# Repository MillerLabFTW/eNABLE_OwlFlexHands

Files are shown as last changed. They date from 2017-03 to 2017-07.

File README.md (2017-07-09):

# eNABLE_OwlFlexHands
**OwlFlex Left and Right Hand Files**  
**Miller Lab Physiologic Systems Engineering and Advanced Materials**  
[Miller Lab](millerlab.rice.edu)  
GitHub Logo

**Documentation**
This repository contains scaled Left OwlFlex and Right OwlFlex Hands from 0.6 to 1.0 scale. Please download the files and measure the relevant dimensions using NetFabb or other softwares. 

**Acknowledgements**
This design was modified from the FlexyHand, which was designed by Gyrobot: http://www.thingiverse.com/thing:380665.

Contributors: Akhil Surapaneni, Chris Vangundy, Justin Tang, Angelo Molina-Rossi, Dr. Gloria Gogola, Jordan Miller

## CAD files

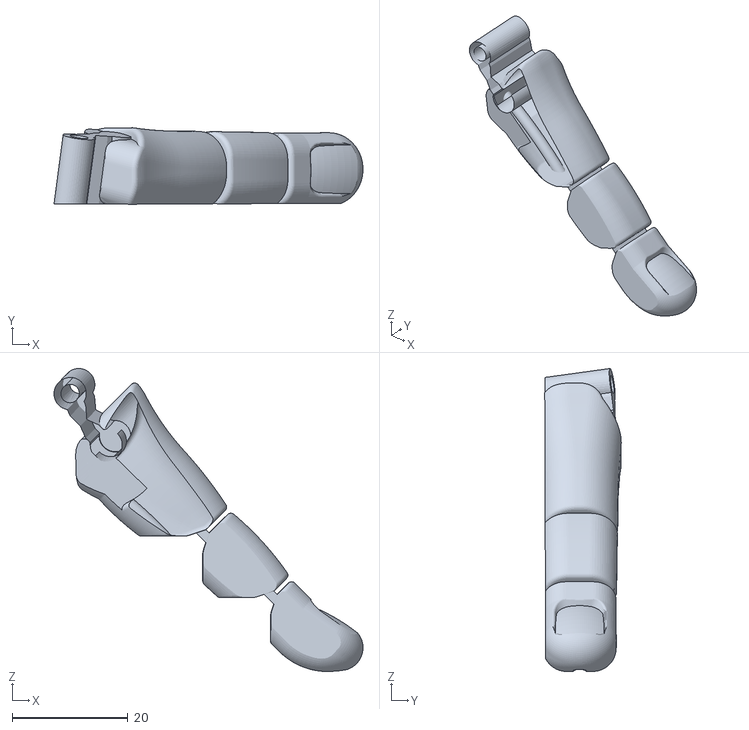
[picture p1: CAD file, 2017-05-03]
0.79 Scale Regular Hinge Fingers/0.79_Regular Hinge Pinky.stl
53.3 x 13.2 x 52.3

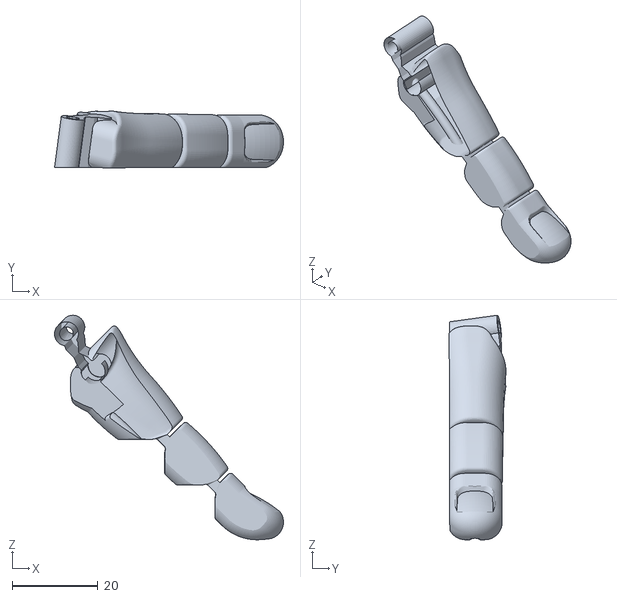
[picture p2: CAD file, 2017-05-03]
0.79 scale Thick Hinge Fingers/0.79_thickhingejointspinky.stl
53.3 x 13.2 x 52.3

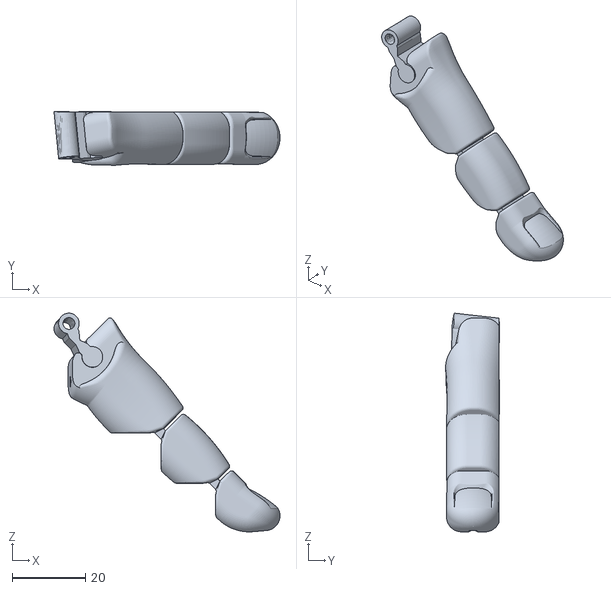
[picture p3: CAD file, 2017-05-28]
0.81 scale Thick Hinge Fingers/0.81_thickhingejointsindex.stl
61.7 x 14.7 x 59.7

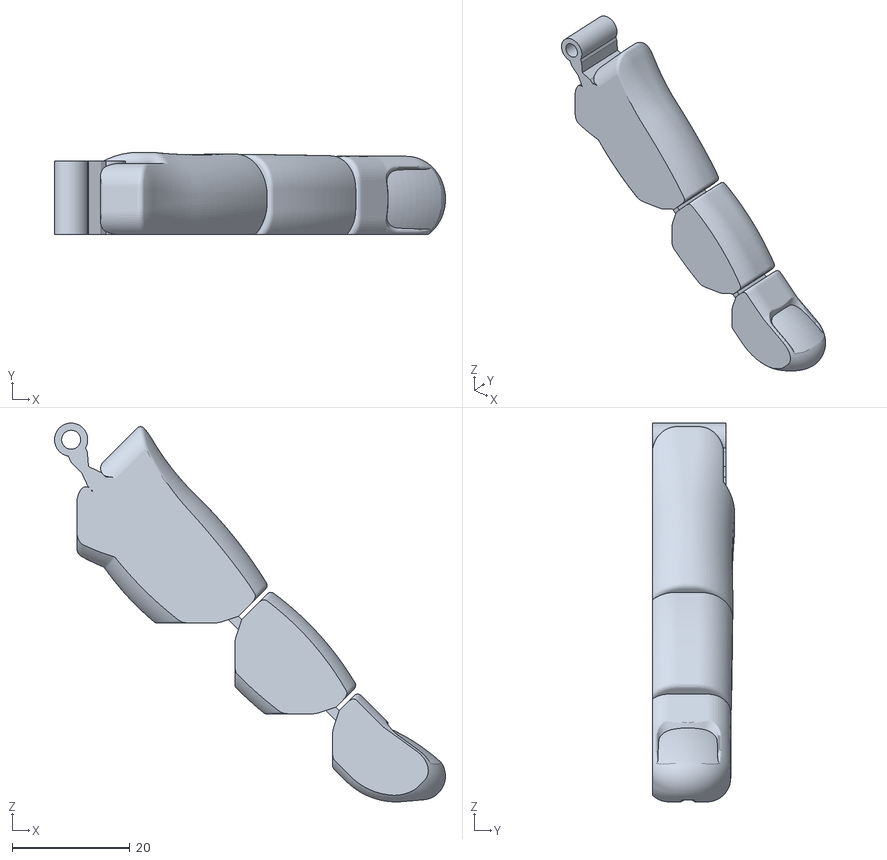
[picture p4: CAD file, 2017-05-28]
0.81 scale_regular hinge fingers/0.81_Regular Hinge Middle Finger .stl
66.5 x 13.9 x 64.4

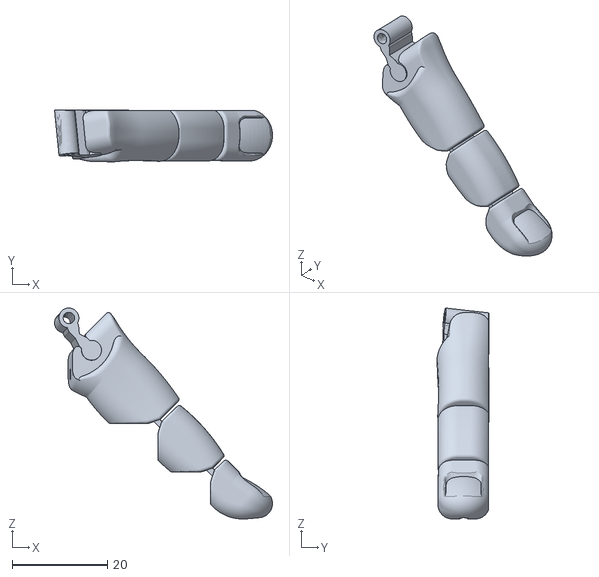
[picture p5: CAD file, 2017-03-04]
Left Hand Owl Flex Palm (0.77-0.84 scale)/0.6 OwlFlex/Flat Index Finger_0.6 .stl
45.7 x 10.9 x 44.2

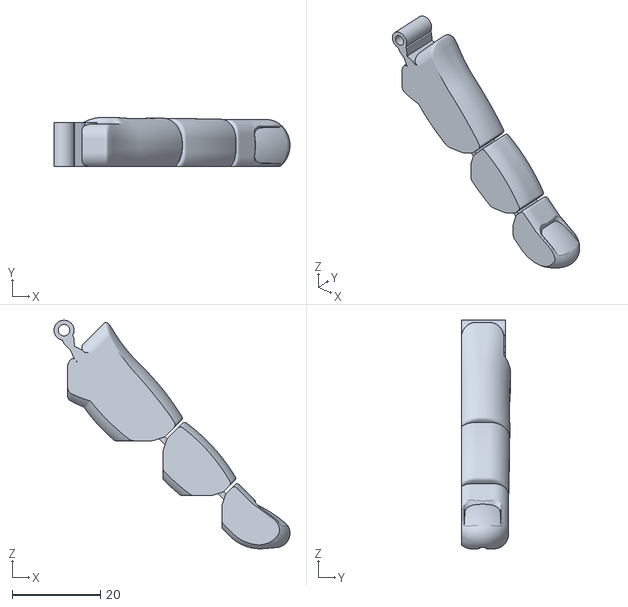
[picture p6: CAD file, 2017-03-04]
Left Hand Owl Flex Palm (0.77-0.84 scale)/0.65 OwlFlex/Flat Middle Finger _0.65.stl
53.4 x 11.2 x 51.7

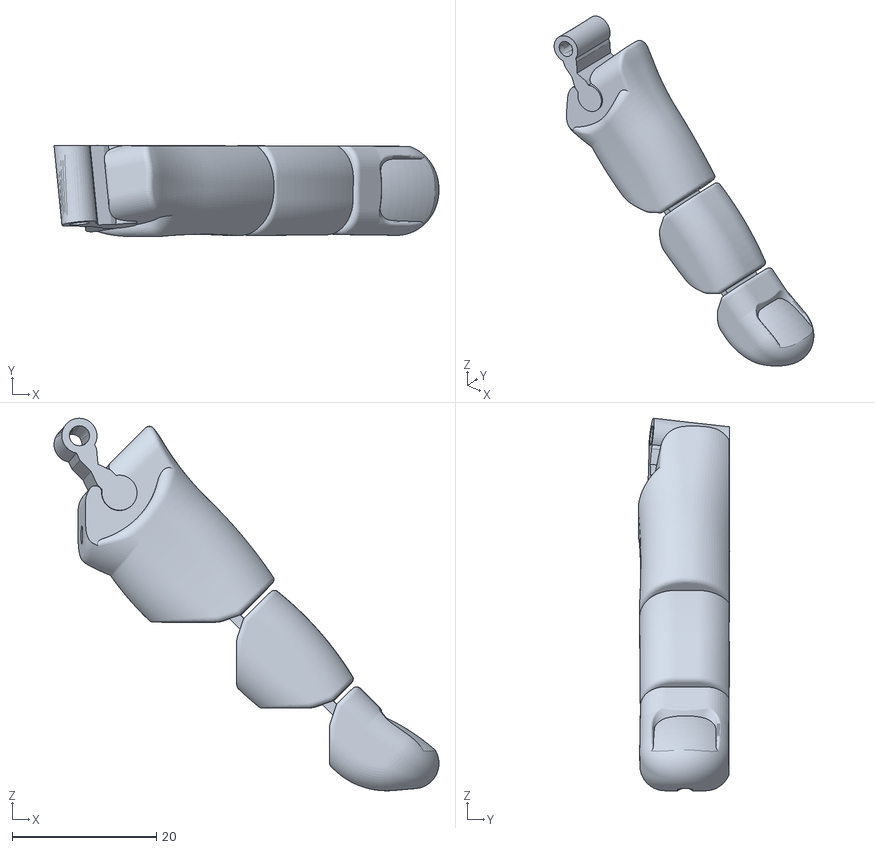
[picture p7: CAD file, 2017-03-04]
Left Hand Owl Flex Palm (0.77-0.84 scale)/0.7 OwlFlex/Flat Index Finger_0.7 .stl
53.3 x 12.7 x 51.6

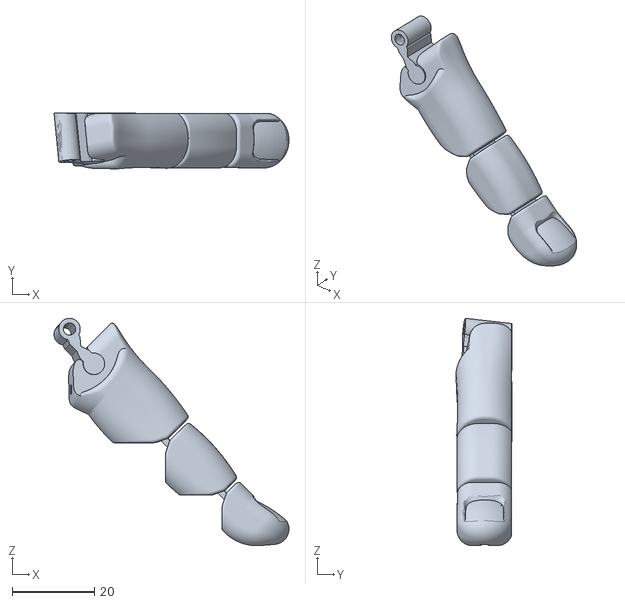
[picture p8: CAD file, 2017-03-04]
Left Hand Owl Flex Palm (0.77-0.84 scale)/0.75 OwlFlex/Flat Index Finger_0.75.stl
57.1 x 13.6 x 55.3

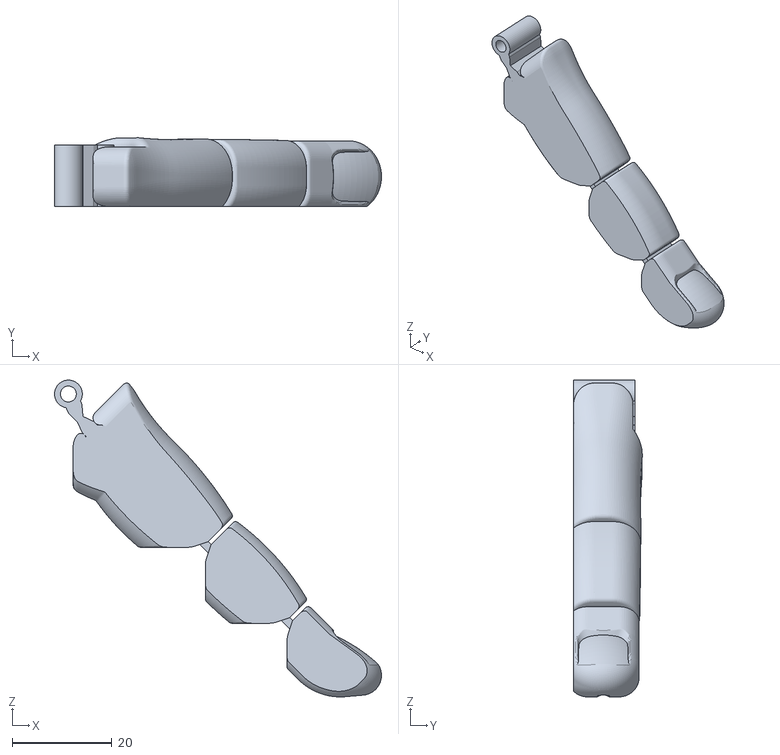
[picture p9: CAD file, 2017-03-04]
Left Hand Owl Flex Palm (0.77-0.84 scale)/0.8 Owl Flex/Flat Middle Finger_0.8.stl
65.7 x 13.8 x 63.6

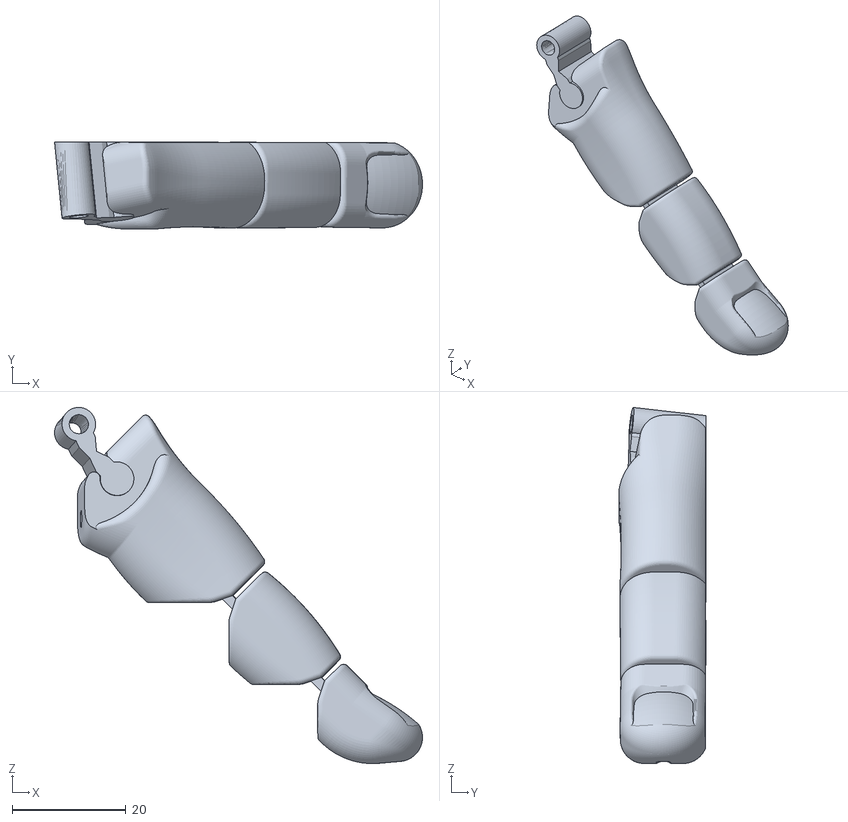
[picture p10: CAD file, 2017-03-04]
Left Hand Owl Flex Palm (0.77-0.84 scale)/0.85 OwlFlex/Flat Index Finger_0.85.stl
64.7 x 15.4 x 62.6

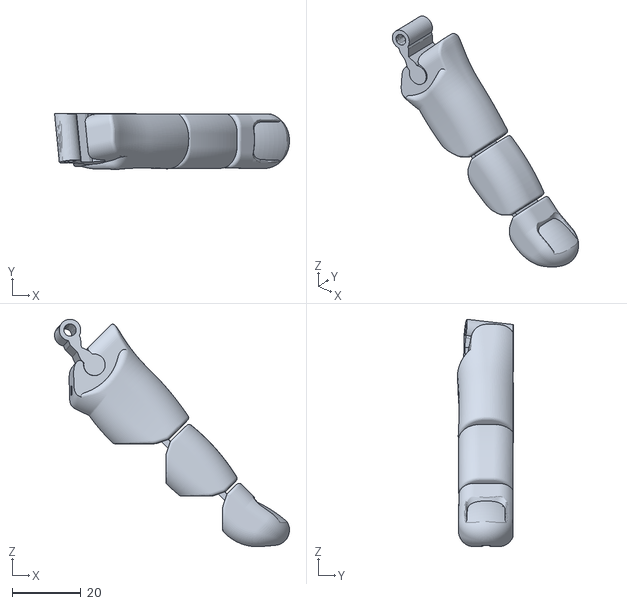
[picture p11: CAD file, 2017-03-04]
Left Hand Owl Flex Palm (0.77-0.84 scale)/0.90 OwlFlex/Flat Index Finger_0.9.stl
68.5 x 16.3 x 66.3

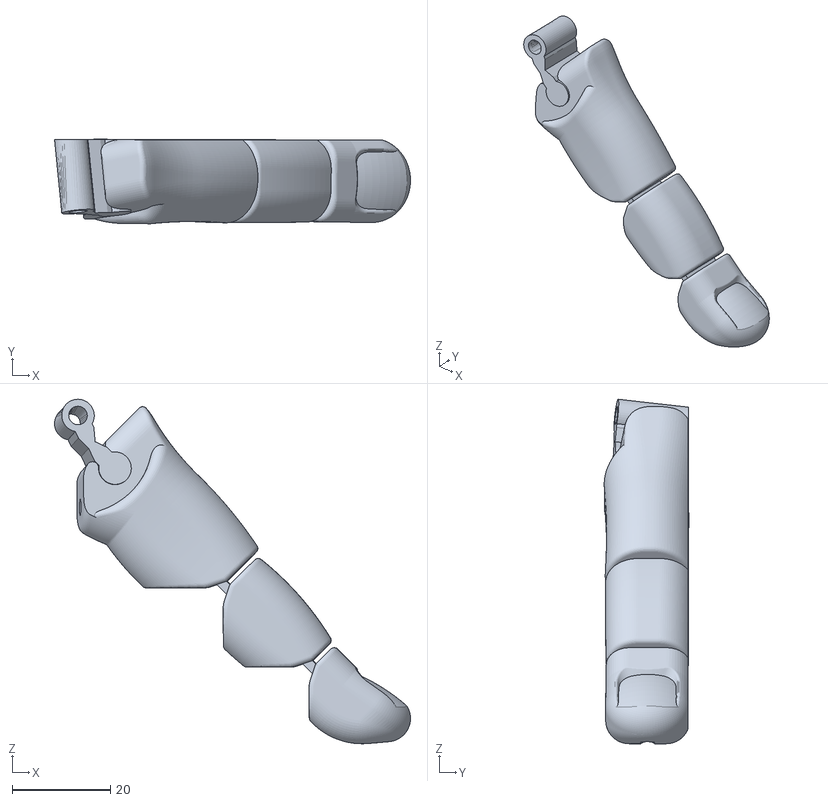
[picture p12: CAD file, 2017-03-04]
Left Hand Owl Flex Palm (0.77-0.84 scale)/0.95 OwlFlex/Flat Index Finger_0.95.stl
72.3 x 17.2 x 70.0

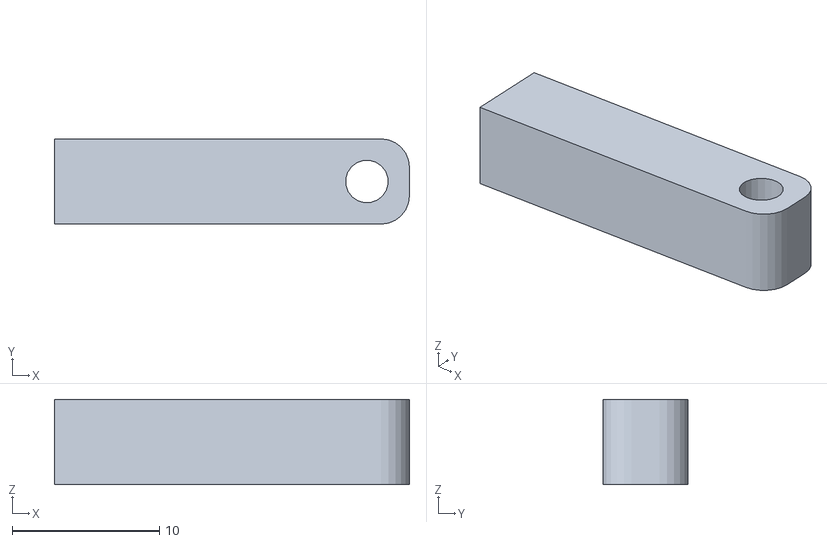
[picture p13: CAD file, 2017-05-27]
Owl Flex Final Design 1.0 Scale/Tensioner-correct-scale.stl
24.1 x 5.78 x 5.78

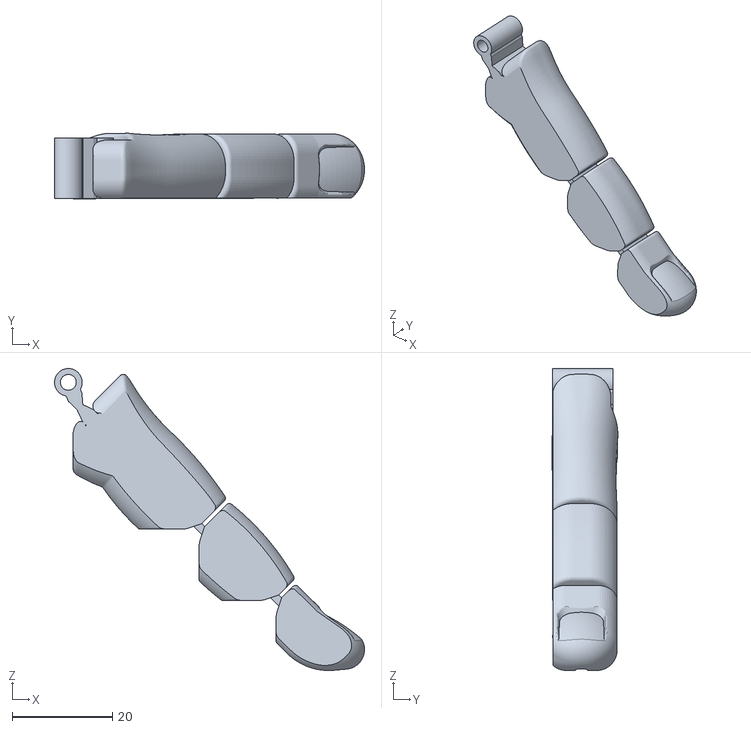
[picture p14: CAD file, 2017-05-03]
0.79 Scale Regular Hinge Fingers/0.79_Regular Hinge Ring Finger.stl
61.8 x 13.1 x 60.2

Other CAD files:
0.79 scale Thick Hinge Fingers/0.79_thickhingejointsthumb.stl
0.81 scale Thick Hinge Fingers/0.81_thickhingejointsthumb.stl
0.81 scale_regular hinge fingers/0.81_Regular Hinge Ring Finger.stl
Left Hand Owl Flex Palm (0.77-0.84 scale)/0.6 OwlFlex/Flat Middle Finger_0.6.stl
0.79 Scale Regular Hinge Fingers/0.79_Regular Hinge Index Finger .stl
0.79 Scale Regular Hinge Fingers/0.79_Regular Hinge Middle Finger .stl
0.79 Scale Regular Hinge Fingers/0.79_Regular Hinge Thumb.stl
0.79 scale Thick Hinge Fingers/0.79_thickhingejointsindex.stl
0.79 scale Thick Hinge Fingers/0.79_thickhingejointsmiddleflat.stl
0.79 scale Thick Hinge Fingers/0.79_thickhingejointsring.stl
0.81 scale Thick Hinge Fingers/0.81_thickhingejointsmiddleflat.stl
0.81 scale Thick Hinge Fingers/0.81_thickhingejointspinky.stl
0.81 scale Thick Hinge Fingers/0.81_thickhingejointsring.stl
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

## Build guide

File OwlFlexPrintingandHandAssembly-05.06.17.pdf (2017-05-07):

OwlFlex Hand Printing and Assembly By Akhil Surapaneni, Chris Vangundy Printing Overview

Part | Filename | Material | Infill | Printer | Extruder Temp | Bed Temp | Print Speed
Gauntlet | Gauntlet-Long-cor rect-scale.stl | PLA | 80% | Ultimaker 2 | 210C | 60 | 50 mm/sec
Fingers (Typical Hand Set) | Regular Hinge Index Finger .stl, Regular Hinge Middle Finger .stl, Regular Hinge Pinky.stl, Regular Hinge Ring Finger.stl, Regular Hinge Thumb.stl | Semiflex | 35% | M2 or Prusa | 235C on M2/ 230C on Prusa | 50C on Prusa/ 40C on M2 | 16.67 on M2 / 30% speed manual override on Prusa
Fingers (Alternate Hand Set) | thickhingejointsind ex.stl, thickhingejointsmi ddleflat.stl, thickhingejointspin ky.stl, thickhingejointsrin g.stl , thickhingejointsth umb.stl | Ninjaflex | 35% | M2 or Prusa | 235C on M2/ 230C on Prusa | 50C on Prusa/ 40C on M2 | 16.67 on M2 / 30% speed manual override on Prusa
Palm | OwlFlexRightHan d.stl or OwlFlexPalm.stl (left hand) | Ninjaflex | 35% | M2 or Prusa | 235C on M2/ 230C on Prusa | 50C on Prusa/ 40C on M2 | 16.67 on M2 / 50% speed manual override on Prusa
Hinges | FFX_-_Flexy-Hing e_Wrist.stl | Ninjaflex | 35% | M2 or Prusa | 235C on M2/ 230C on Prusa | 50C on Prusa/ 40C on M2 | 16.67 on M2 / 50% speed manual override on Prusa

Pins | Tensioner-correct-
scale.stl
PLA | 80% | Ultimaker 2 | 210C | 60 | 50 mm/sec

Parts:
Please download the following files from MillerLabFTW/eNABLE_OwlFlexHands/Owl Flex Final Design 1.0 Scale on Github

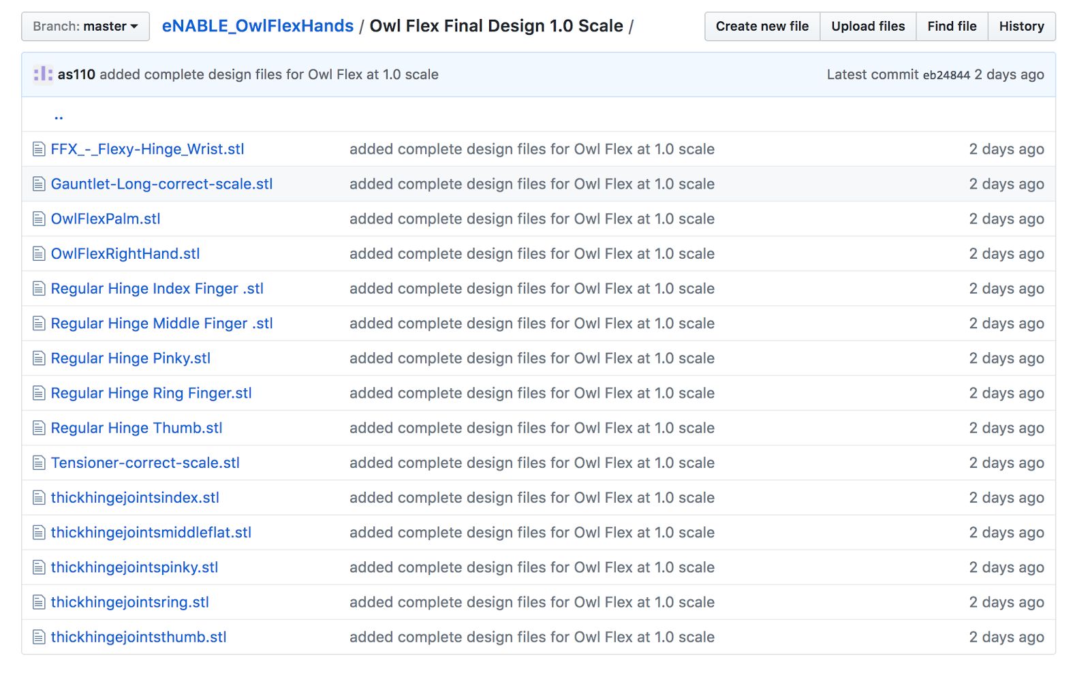
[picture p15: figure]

Fig.1: Github Folder with Design Files
- Palm: OwlFlexRightHand.stl or OwlFlexPalm.stl (left hand)
- Gauntlet: Gauntlet-Long-correct-scale.stl
- Fingers (please download either the Regular Hinge or Thick Hinge Fingers)
- Regular Hinge Fingers:Regular Hinge Index Finger .stl, Regular Hinge Middle Finger .stl, Regular Hinge Pinky.stl, Regular Hinge Ring Finger.stl, Regular Hinge Thumb.stl
- thickhingejointsindex.stl, thickhingejointsmiddleflat.stl, thickhingejointspinky.stl, thickhingejointsring.stl, thickhingejointsthumb.stl
- Wrist Hinges: FFX_-_Flexy-Hinge_Wrist.stl
- Tensioner Pin: Tensioner-correct-scale.stl
Scaling
Please scale the palm so that the patient’s orthoplast socket is a snug fit inside of it. At 1.0 scale, the palm is 65mm across the wrist as seen in Fig.2 below.Please use one of the shoebox palms for reference.

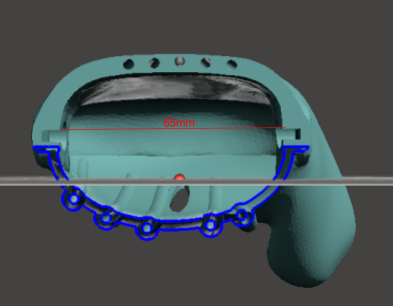
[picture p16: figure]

Fig.2: Width of Palm across Wrist Please download the correct sized palm from the eNABLE_OwlFlexHands repository. For the other parts, please scale them to the same scale as the palm.
IN THE FUTURE: We want to be able to match the fingers scale so that they are the same size as the patient’s biological fingers. Please update the protocol once we figure out how to do this.
Slicing
- Palm: Orient the hand as seen in the picture below (Fig.3) and please don’t add any support. It is printed with 35% infill with Ninjaflex.

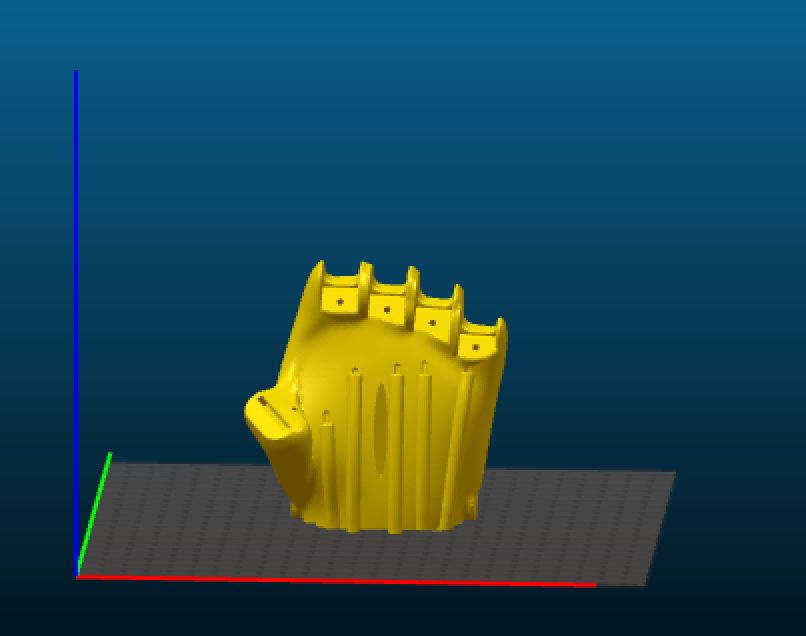
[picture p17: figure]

Fig.3 Palm Printing

When printing on M2, use the M2 profile.
When printing on Prusa, please consult the “Printing Ninjaflex on Prusa i3.docx” file found on the server at People→ eNABLE→ Logistics and Overview. Use the 0.2mm Normal profile and change the infill to 35% (Fig. 4)

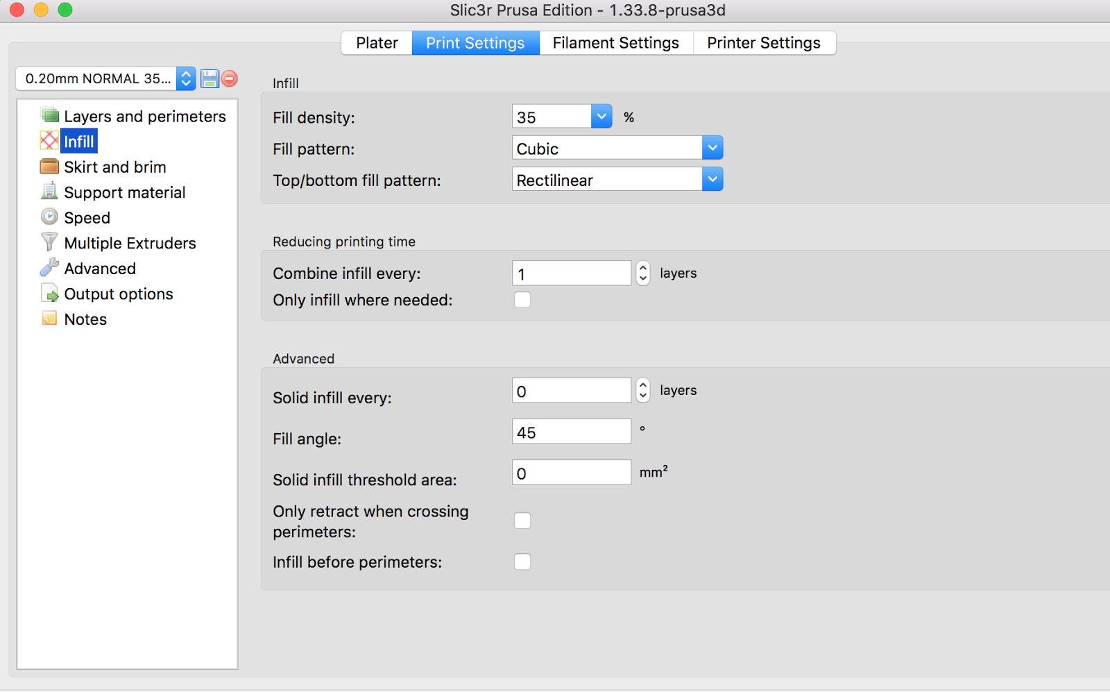
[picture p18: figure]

Fig. 4: Palm Infill Density on Prusa
- Fingers: printed with 35% infill
- When printing Regular Hinge fingers, please insert Semiflex Filament into both the M2 and Prusa printers. Please use the Semiflex profile on the M2 and the 0.2mm Normal 35% Infill profile on the Prusa that we have created for the palm.
- When printing Thick Hinge fingers, please insert Ninjaflex Filament into both the M2 and Prusa printers. Please the M2 profile on the M2 and 0.2mm Normal 35% Infill profile on the Prusa
- When printing fingers on the Prusa, make sure that the manual override speed is set to 30% and the Live Z offset is set to -0.675mm. For more info on where to find those settings, please consult the “Printing Ninjaflex on Prusa” protocol Please orient the fingers so that the flat side is touching the print surface as seen below (Fig.5) and (Fig.6)

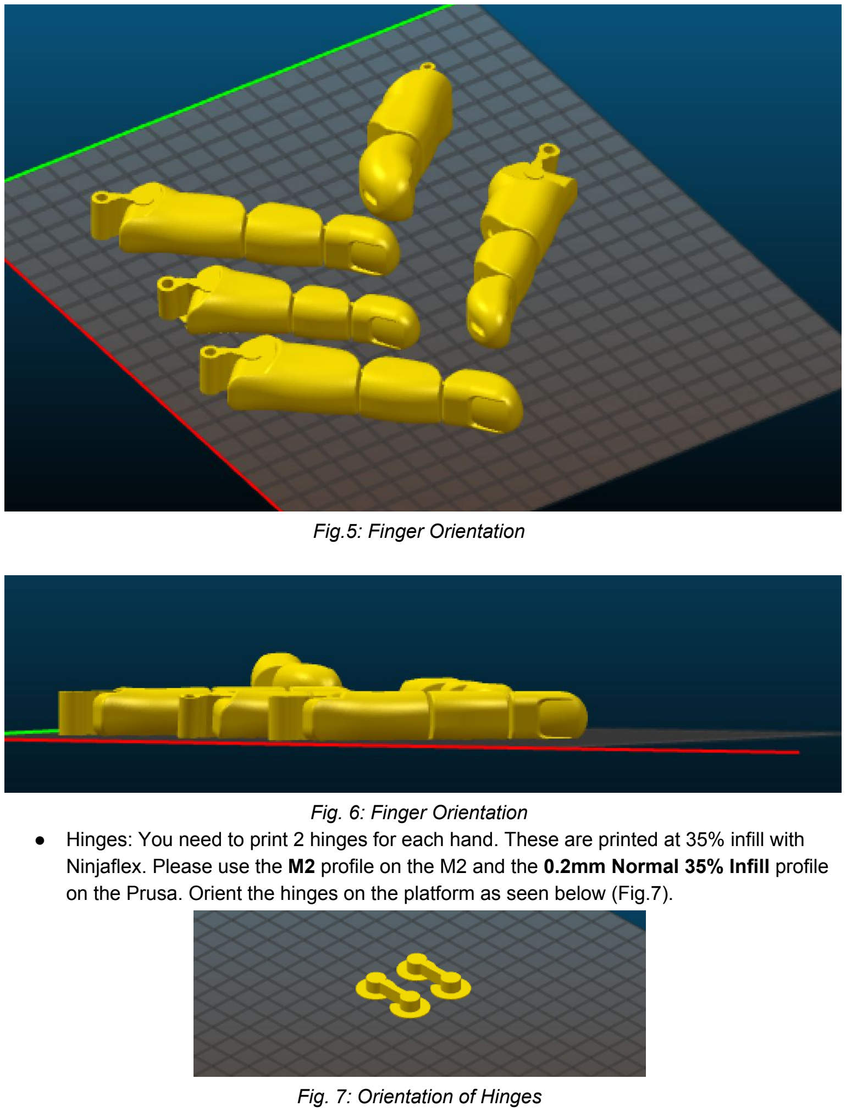
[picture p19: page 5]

Fig.5: Finger Orientation

Fig. 6: Finger Orientation
- Hinges: You need to print 2 hinges for each hand. These are printed at 35% infill with Ninjaflex. Please use the M2 profile on the M2 and the 0.2mm Normal 35% Infill profile on the Prusa. Orient the hinges on the platform as seen below (Fig.7).

Fig. 7: Orientation of Hinges

- Gauntlet: Please print the Gauntlet at 80% infill and use a Brim when printing it. The gauntlet is printed on Ultimaker with PLA filament, so please use Cura to slice the file. The key print settings can be seen in the figure below (Fig.8).

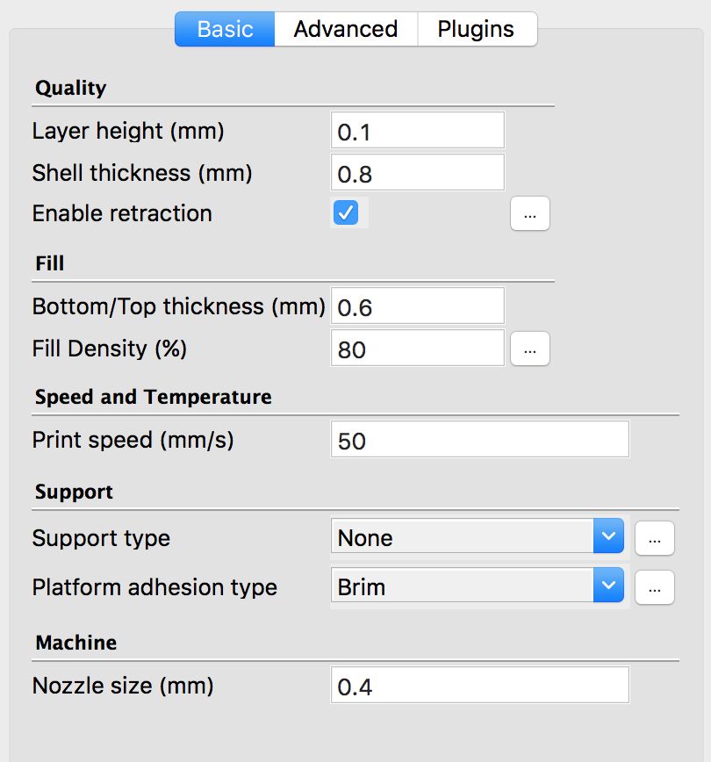
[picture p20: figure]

Fig.8: Gauntlet Printing Profile The orientation of the gauntlet on the platform can be seen in the figure below (Fig.9).

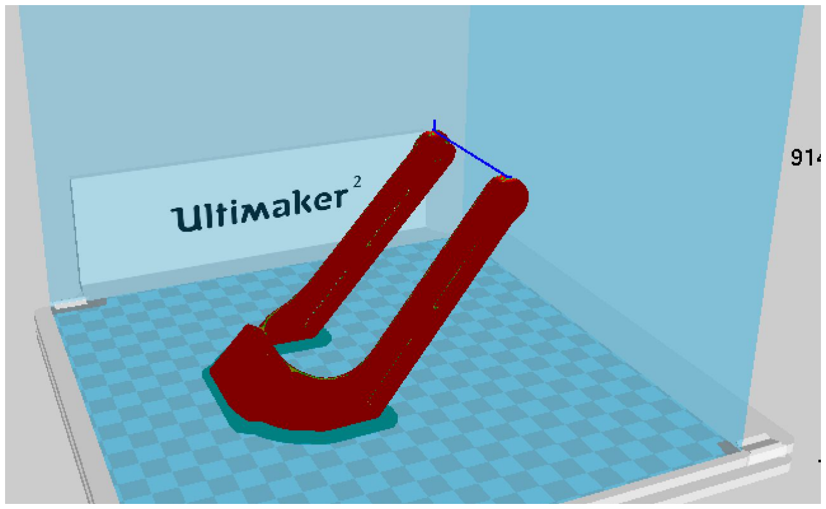
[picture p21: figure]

Fig.9: Gauntlet Printing Orientation
- Pins: You need 5 pins per hand. These are printed with the Ultimaker using PLA. Please use the same profile as you used for the Gauntlet. Orient the pins as seen below (Fig.10).

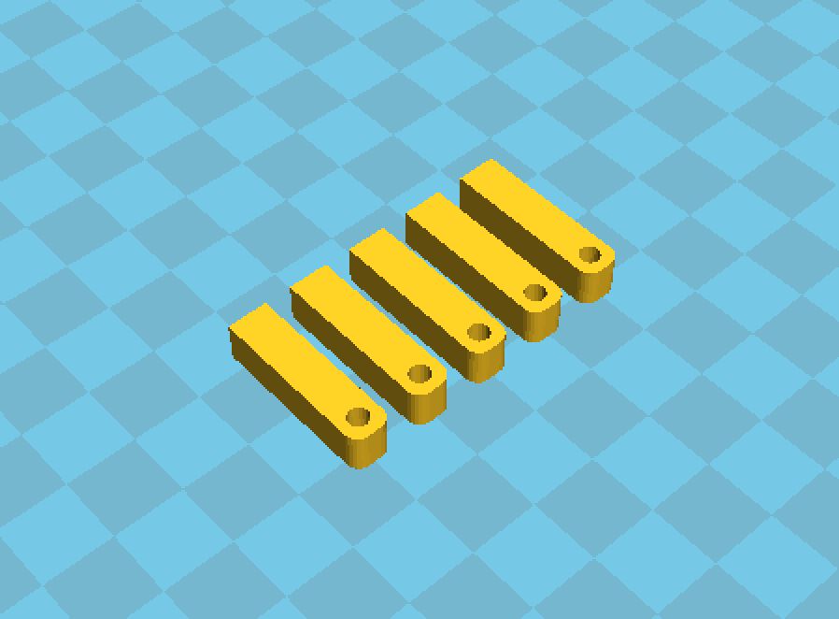
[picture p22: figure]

Fig.10: Orientation of Pins Printing
- Printing on the M2:
- First, heat up the extruder in the Machine control Panel to 230C. As this happens, clean out the bed with water and Isopropyl Alcohol (IPA)
- Retract the filament out of the nozzle
- Pull out the nozzle and push 1.75mm PLA into the nozzle to clean any possible clogs.
- Put the nozzle back into the extruder and hit the Extrude button on Machine Control Panel as you feed in Ninjaflex or Semiflex. Please hold the filament at the top as it feeds into the extruder. Once all the PLA has been cleared out, hit Prepare to Print on Simplify 3D
- Apply glue onto the bed using a glue stick before it starts printing. Stick around for the first few layers.
- Printing on Prusa: Please follow the instructions on the “Printing Ninjaflex on Prusa i3.docx”
After Printing, you should have all of the pieces seen below (Fig.11)

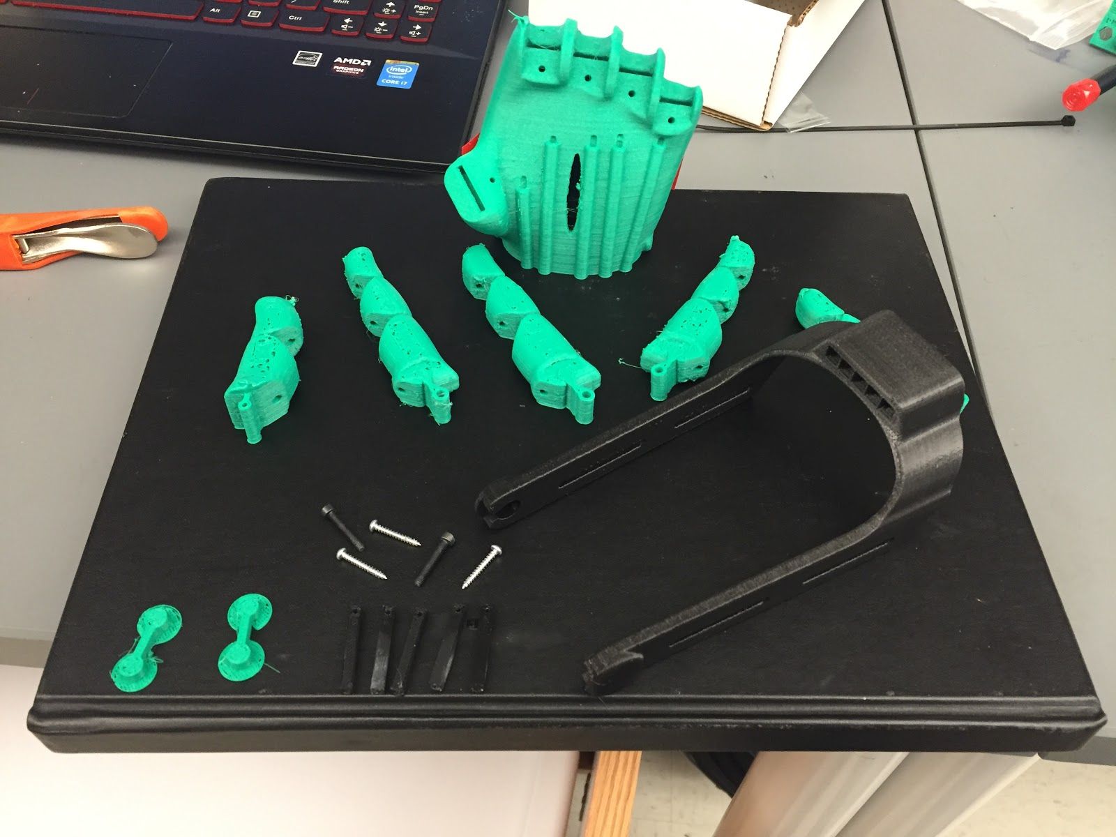
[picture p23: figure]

Fig.11: Printed Parts
Assembly
- Using a pair of pliers, attach the fingers to their respective locations on the palm.

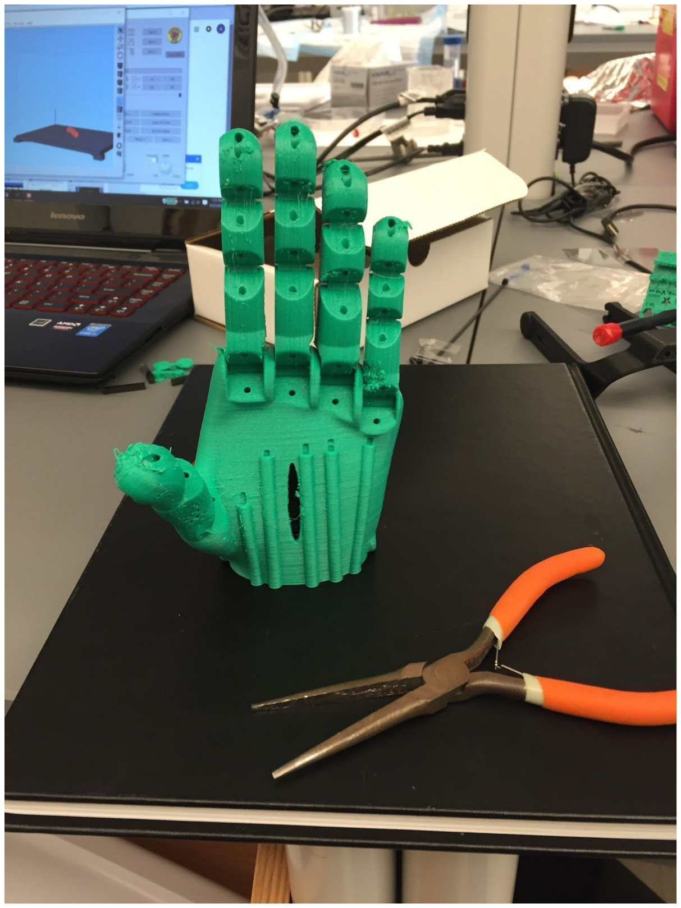
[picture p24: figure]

- Strip 5 1 inch segments of 22 AWG wire and keep the external casing. This prevents the filament of each wire from cutting through the top of the phalanx over time. Using super glue, attach each segment into the proximal phalanx of each finger (Fig.12)

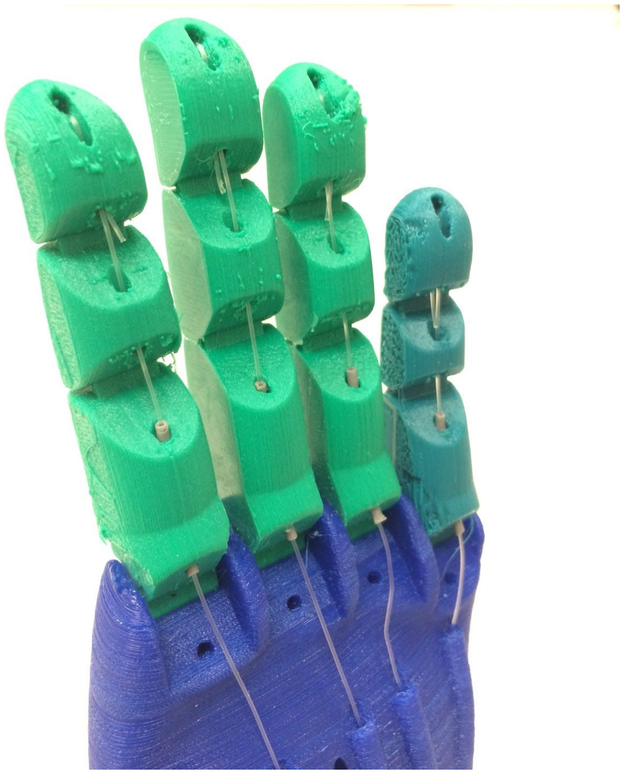
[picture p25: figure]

Fig.12: AWG Wire Tubing

- Super glue the two hinges into the sockets at the bottom of the hand, and after they have set, glue the other side of each hinge into the gauntlet
- Insert the tensioner pins into the slots on the gauntlet and secure with a bolt.
A picture of the above two steps can be seen in Fig. 14
- Stringing the hands
- Tie a non-slip knot onto the top of the finger following this tutorial: https://www.youtube.com/watch?v=hxQ3IsNwNx4
- The following picture (Fig.13) is a good graphic for how to tie the non-slip knot.

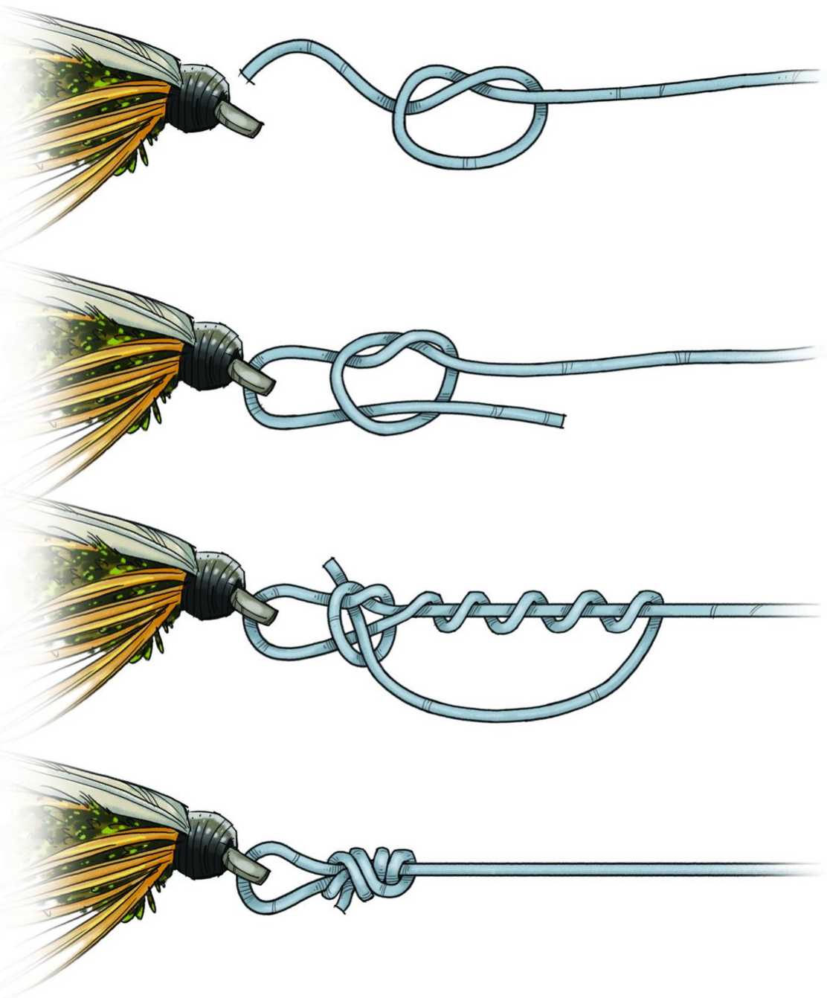
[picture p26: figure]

Fig.13: Non-Slip knot

- When stringing a hand for patients, we will tension the hand once the patient has put it on.
- When stringing a hand for testing a demonstration purposes, follow the steps below.
- Push the string through the channels at the base of the palm and tie knots at the gauntlet as seen below.

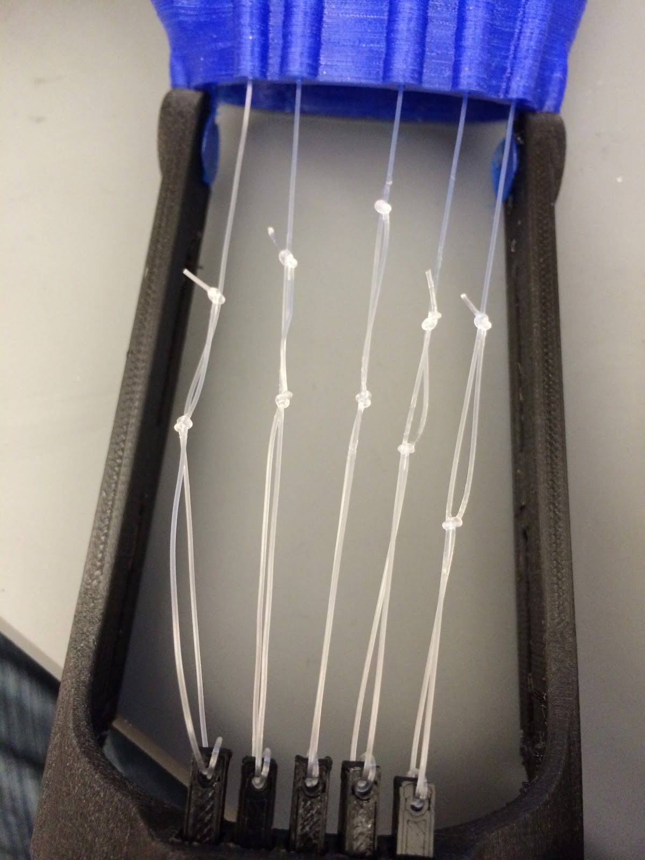
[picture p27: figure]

Fig.14: Hinges, Pins, and depiction of knots at Gauntlet level
- Tie them so that the fingers close at 20 degrees of wrist extension
- Use Table 1 for reference for the length of the tensioning strings so that the fingers close at 20 degrees of wrist extension. This applies when each finger is printed at 0.77 scale, but this can be a rough guide for other sizes as well.
Finger | Length (cm)
Thumb | 13.25

Forefinger | 13.5
Middle Finger | 13.5
Ring Finger | 13.6
Pinky Finger | 15.1
Table 2: Proper lengths of tensioning for each finger
- Once the hands are assembled, disinfect the entire hand with 70% ethanol

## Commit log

2017-03-04 Added palm sizes by 0.1 increments from 0.77 to 0.85 scale
    [Flat Index Finger_0.6 .stl, Flat Index Finger_0.65.stl, Flat Index Finger_0.7 .stl, Flat Index Finger_0.75.stl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]
2017-04-27 added thick hinge finger files
    [Flat Index Finger_0.6 .stl, Flat Index Finger_0.65.stl, Flat Index Finger_0.7 .stl, Flat Index Finger_0.75.stl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]
2017-04-27 added thick hinge files
    [0.79_thickhingejointsindex.stl, Flat Index Finger_0.6 .stl, Flat Index Finger_0.65.stl, Flat Index Finger_0.7 .stl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]
2017-04-27 added 0.79 scale thick hinge fingers
    [0.79_thickhingejointsmiddleflat.stl, 0.79_thickhingejointspinky.stl, 0.79_thickhingejointsring.stl]
2017-05-03 added 0.79 scale regular hinge fingers
    [0.79_Regular Hinge Index Finger .stl, 0.79_Regular Hinge Middle Finger .stl, 0.79_Regular Hinge Pinky.stl, 0.79_Regular Hinge Ring Finger.stl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]
2017-05-04 added complete design files for Owl Flex at 1.0 scale
    [FFX_-_Flexy-Hinge_Wrist.stl, Gauntlet-Long-correct-scale.stl, Regular Hinge Index Finger .stl, Regular Hinge Middle Finger .stl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]
2017-05-05 Added Owl Flex Printing and Assembly Protocol
2017-05-07 added the Owl Flex Printing and Assembly Document
2017-05-07 updated OwlFlex Printing and Assembly Doc
2017-05-27 matched tensioner scale to gauntlet scale
    [Tensioner-correct-scale.stl]
2017-05-28 added 0.81 thick and regular hinge fingers
    [0.81_Regular Hinge Index Finger .stl, 0.81_Regular Hinge Middle Finger .stl, 0.81_Regular Hinge Ring Finger.stl, 0.81_Regular Hinge Thumb.stl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]
2017-05-28 added thick hinge and regular hinge fingers for 0.79 and 0.81 scale
    [0.79_Regular Hinge Index Finger .stl, 0.79_Regular Hinge Middle Finger .stl, 0.79_Regular Hinge Pinky.stl, 0.79_Regular Hinge Ring Finger.stl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]
